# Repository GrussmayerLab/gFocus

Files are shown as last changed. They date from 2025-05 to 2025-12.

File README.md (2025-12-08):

# Fairly Good Focus (fgFocus)

**fgFocus** is an active focus-lock system designed to maintain sharp focus during extended imaging experiments, such as single-molecule and live-cell imaging. It corrects axial drift (movement along the Z-axis) that can occur over time, ensuring your sample stays perfectly in focus.

This project is inspired by similar systems like qgFocus and pgFocus and follows the same naming convention.

Estimated cost for this project is around €160.

## Key Features

- Real-time focus correction  
- Micro-Manager compatible  
- Flexible hardware support: works with any motorized Z-stage controllable through Micro-Manager  

## How It Works

1. An infrared laser beam is aimed slightly off-center into the objective lens.  
2. The beam reflects off the coverslip (glass slide) at the bottom of the sample.  
3. When the sample moves up or down (axial drift), the reflected beam shifts sideways.  
4. A light-array sensor detects this lateral shift by measuring the intensity profile of the reflected beam.  
5. The system calculates the amount of drift using a Gaussian fit to find the center of the beam.  
6. A feedback loop adjusts the Z-position of the stage to return the beam to its original position — restoring focus. 

---

## Table of Contents

* [Fairly Good Focus (fgFocus)](#fairly-good-focus-fgfocus)

  * [Key Features](#key-features)
  * [How It Works](#how-it-works)
  * [Getting Started](#getting-started)
    * [Hardware Setup](#hardware-setup)
    * [Firmware Setup](#firmware-setup)
    * [Software Setup](#software-setup)
  * [Usage](#usage)
  * [Note](#note)
  * [Contribution](#contribution)
  * [License](#license)

---

## Getting Started

### Hardware Setup

1. The **PCB** directory contains the full **Gerber set** for fabrication, plus the **schematic** and **board layout** inside the `fgFocus` subfolder. The project was created in **KiCad**.
2. At **JLCPCB**, upload the `Gerber.rar` archive and select **PCB Assembly**.
3. When prompted, provide the `bom.csv` and `fgFocus-top-pos.csv` files to complete the assembly configuration.
4. Some parts cannot be machine-assembled and must be sourced and soldered manually. These items are listed in `bom_external_components.csv`.
5. The **enclosure design** is located in the `enclosure` directory with a `bom.csv` to source the enclosure. 
6. In the `enclosure` directory you can find a `REAMDE` that explains the assembly of all components.

### Firmware Setup

1. fgFocus uses the [XIAO SAMD21 microcontroller](https://nl.mouser.com/ProductDetail/Seeed-Studio/102010328?qs=GBLSl2AkirtQWO8CTzEK9g%3D%3D&srsltid=AfmBOoqHyFkl2Qpgyily5YNBzPaesjcrrXG1Ro79G8migozdgHgJccld).  
2. Follow this [getting started tutorial](https://wiki.seeedstudio.com/Seeeduino-XIAO/) to program the board using the `fgFocus.ini` file.

### Software Setup

1. **Install Micro-Manager 2.0**  
   - Download and install the latest version of [Micro-Manager 2.0](https://download.micro-manager.org/nightly/2.0/Windows/).  
   - Copy the precompiled `EMU` folder (provided) into the root directory of Micro-Manager.

2. **Install the EMU Plugin** (for editing or customizing the interface)  
   - Follow the instructions here: [EMU Guide](https://jdeschamps.github.io/EMU-guide/)

3. **Install the fgFocus Plugin**  
   - Copy the `FocusLock.jar` file into the `EMU` folder in your Micro-Manager directory.

4. **Install the Device Adapter**  
   - Copy the `mmgr_dal_fgFocus.dll` file into the root directory of Micro-Manager.  
   - To modify or rebuild the adapter:  
     - Follow the [Micro-Manager Visual Studio setup guide](https://micro-manager.org/Visual_Studio_project_settings_for_device_adapters)  
     - Place `.h` files in the **header** folder and `.cpp` files in the **source** folder.  
     - Compile the project and place the resulting `.dll` file into the Micro-Manager root directory.

## Usage

1. Connect the fgFocus system to your PC using a USB-C cable.
2. Create a folder called `fgFocus` in the root of Micro-Manager.  
2. In Micro-Manager, go to **Device > Hardware Configuration Wizard** and create a new config file to only add `fgFocus` and save it in the `fgFocus` folder. Make sure you select a baudrate of 115200.
3. Launch the plugin: **Plugins > User Interface > EMU** — the fgFocus control panel will open. Ignore, the warning that it is not configured, `fgFocus` runs on a separate MMCore instance.

You should see the following interface:

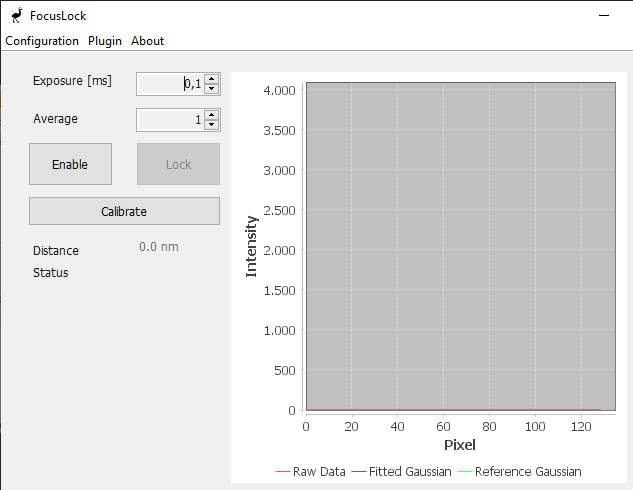
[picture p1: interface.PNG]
fgFocus


Now you're ready to go!

In the interface:
- You can adjust the **exposure time** and **averaging** for the light-array sensor.
- Press the `Enable` button to monitor pixel data from the sensor.
- Use the `Calibrate` button to run a calibration script that determines the relationship between pixel position and Z-distance.
- Once calibration is complete, the `Lock` button becomes available, activating the focus lock.

**Happy Imaging!**

## Note
To adjust the **number of steps** or the **step size** used in the calibration script, open `CalibrateTask.java` and modify the following variables:

```java
private final int numSteps = 5;
private final double stepSizeUm = 1;
```

## Contribution

Contributions are welcome. Whether you're enhancing firmware stability, refining hardware design, or extending the MicroManager plugins, focused pull requests with clear explanations help keep the project maintainable. Open an issue if you'd like to discuss a feature or improvement before implementing it.

## License

Software in this project is licensed under the MIT License and hardware is licensed under CERN OHL - see `LICENSE` file for details in the licenses folder.

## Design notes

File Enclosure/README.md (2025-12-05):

## Assembly Instructions for `fgFocus`

1. **Attach the light sensor**
   Insert the light sensor into the PCB so that the mounting holes on both parts line up correctly.

2. **Install the spacers**
   Place the four spacers onto the mounting posts on the bottom half of the enclosure. These keep the PCB from resting directly on the surface. Ensure the USB-C port is positioned so it lines up with the enclosure’s USB opening.

3. **Insert the bolts**
   From underneath the enclosure, insert the four M3 bolts upward so they pass through the enclosure, the spacers, and the PCB.

4. **Close the enclosure**
   Place the top cover onto the enclosure, then secure it by tightening the provided screws and nuts.

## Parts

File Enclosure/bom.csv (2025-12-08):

enclosure | https://www.digikey.nl/nl/products/detail/hammond-manufacturing/1590LLBBK/2360754
bolts | https://www.amazon.nl/Walfront-Schroefset-koolstofstaal-schroefdraad-gedeeltelijk/dp/B075SDDRVH?__mk_nl_NL=%C3%85M%C3%85%C5%BD%C3%95%C3%91
nuts | https://www.amazon.nl/schroefdraad-zeskantmoeren-koolstofstaal-stopmoeren-zelfborgende/dp/B0C6SM43H6
spacer | https://www.amazon.nl/SWTYExt-afstandhouders-afstandshulzen-wandisolatie-afstandhulzen/dp/B0CWXSTRKZ

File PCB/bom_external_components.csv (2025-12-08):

U7 | XIAO-SAMD21-SAMD21 | https://www.seeedstudio.com/Seeeduino-XIAO-Arduino-Microcontroller-SAMD21-Cortex-M0+-p-4426.html
J3 | DF11-12DS-2DSA(06) | https://eu.mouser.com/ProductDetail/Hirose-Connector/DF11-12DS-2DSA06?qs=Ux3WWAnHpjDo2sVdM55Wrg%3D%3D
Line Sensor | TSL1401-DB | https://abra-electronics.com/robotics-embedded-electronics/parallax-en/parallax-sensors/28317-parallax-tsl1401-linescan-imaging-sensor-daughterboard-28317.html

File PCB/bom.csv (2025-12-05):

Comment | Designator | Footprint | LCSC
1.5k" | R5 | Resistor_SMD:R_0805_2012Metric | C4310
100p | C15 | Capacitor_SMD:C_0805_2012Metric | C1790

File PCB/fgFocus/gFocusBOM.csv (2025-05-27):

Reference | Value | Datasheet | Footprint | Qty | DNP
C1,C2,C5,C6,C7,C20,C21,L1,L2 | 10u | ~ | -- mixed values -- | 9
C3,C4,C24 | 10n | ~ | Capacitor_SMD:C_0805_2012Metric | 3
C8,C9,C10,C12,C14,C17,C18,C19 | 100n | ~ | Capacitor_SMD:C_0805_2012Metric | 8
C15 | 100p | ~ | Capacitor_SMD:C_0805_2012Metric | 1
C16,C22,C23 | 1u | ~ | Capacitor_SMD:C_0805_2012Metric | 3
C25 | 4.5n | ~ | Capacitor_SMD:C_0805_2012Metric | 1
D1 | PMEG2005EL | ~ | Diode_SMD:D_SOD-882 | 1
J1 | FTSH-105-01-F-DV-P-TR |  | FTSH-105-01-F-DV-P-TR:SAMTEC_FTSH-105-01-F-DV-P-TR | 1
J2 | Conn_Coaxial | ~ | Connector_Coaxial:SMA_Amphenol_132289_EdgeMount | 1
J3 | Conn_02x06_Counter_Clockwise | ~ | Connector_Hirose:Hirose_DF11-12DP-2DSA_2x06_P2.00mm_Vertical | 1
J4 | USB_B_Micro | ~ | Connector_USB:USB_Micro-B_Molex-105017-0001 | 1
R1,R4,R6,R7 | 10k | ~ | Resistor_SMD:R_0805_2012Metric | 4
R2,R3 | 93.1k | ~ | Resistor_SMD:R_0805_2012Metric | 2
R5 | 1.5k | ~ | Resistor_SMD:R_0805_2012Metric | 1
R8 | 1M | ~ | Resistor_SMD:R_0805_2012Metric | 1
U1 | NMA0515SC | http://power.murata.com/data/power/ncl/kdc_nma.pdf | Converter_DCDC:Converter_DCDC_Murata_NMAxxxxSC_THT | 1
U2 | TPS7A3001DGNT |  | TPS7A3001DGNT:SOP65P490X110-9N | 1
U3 | TPS7A4901DGNR |  | TPS7A3001DGNT:SOP65P490X110-9N | 1
U4 | AD5761RBRUZ-RL7 |  | AD5761RBRUZ-RL7:SOP65P640X120-16N | 1
U5 | ATSAMD21G18A-A | http://ww1.microchip.com/downloads/en/DeviceDoc/SAM_D21_DA1_Family_Data%20Sheet_DS40001882E.pdf | Package_QFP:TQFP-48_7x7mm_P0.5mm | 1
U6 | IP4234CZ6 | https://assets.nexperia.com/documents/data-sheet/IP4234CZ6.pdf | Package_TO_SOT_SMD:SOT-23-6 | 1
U8 | LDK130-32_SOT23_SOT353 | http://www.st.com/content/ccc/resource/technical/document/datasheet/29/10/f7/87/2f/66/47/f4/DM00076097.pdf/files/DM00076097.pdf/jcr:content/translations/en.DM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 | Package_TO_SOT_SMD:SOT-23-5_HandSoldering | 1

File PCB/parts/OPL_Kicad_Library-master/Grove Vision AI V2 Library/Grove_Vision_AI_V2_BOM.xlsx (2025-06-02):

Layer Jump | Number | Name | Specification | Operating Temperature | MPN Code | Quantity | Base | Plug Position | Process
N | 301010000 | SMD RES 0R-5%-1/16W;0402 |  | -55°C to 155°C | RC0402JR-070RL | 3 | 1 | R29,R30,R39 | SMT1
N | 301010004 | SMD RES 10K-5%-1/16W;0402 |  | -55°C to 155°C | RC0402JR-0710KL | 7 | 1 | R5,R7,R8,R23,R24,R31,R38 | SMT1
N | 301010008 | SMD RES 510K-5%-1/16W;0402 |  | -55°C to 155°C | RC0402JR-07510KL | 1 | 1 | R35 | SMT1
N | 301010456 | SMD RES 100K-1%-1/16W;0402 |  | -55°C to 155°C | RC0402FR-07100KL | 7 | 1 | R6,R10,R11,R16,R32,R33,R37 | SMT1
N | 301010495 | SMD RES;5.1K-1%-1/16W;0402 |  | -55°C to 155°C | RC0402FR-075K1L | 3 | 1 | R2,R3,R36 | SMT1
N | 301010746 | SMD RES 2.2K-1%-1/16W;0402 |  | -55°C to 155°C | RC0402FR-072K2L | 10 | 1 | R1,R4,R13,R14,R15,R19,R20,R21,R22,R40 | SMT1
N | 301011331 | SMD RES 22.1K-1%-1/16W;0402 |  | -55°C to 155°C | RC0402FR-0722K1L | 2 | 1 | R26,R34 | SMT1
N | 302010004 | SMD CAP Ceramic 100nF-16V-10%-X7R;0402 |  | -55°C to 125°C | CC0402KRX7R7BB104 | 18 | 1 | C5,C8,C13,C20,C21,C22,C23,C24,C25,C26,C27,C29,C30,C31,C32,C35,C36,C39 | SMT1
N | 302010006 | SMD CAP Ceramic 10nF-50V-10%-X7R;0402 |  | -55°C to 125°C | CC0402KRX7R9BB103 | 1 | 1 | C3 | SMT1
N | 302010049 | SMD CAP Ceramic 12pF-50V-5%-NPO;0402 |  | -55°C to 125°C | CC0402JRNPO9BN120 | 2 | 1 | C14,C15 | SMT1
N | 302010051 | SMD CAP Ceramic 220nF-16V-10%-X7R;0402 |  | -55°C to 125°C | CC0402KRX7R7BB224 | 1 | 1 | C16 | SMT1
N | 302010407 | SMD CAP Ceramic 4.7uF-10V-10%-X5R;0402 |  | -55°C to 85°C | CC0402KRX5R6BB475 | 7 | 1 | C4,C6,C7,C9,C10,C28,C34 | SMT1
N | 302010519 | SMD CAP Ceramic 10uF-10V-20%-X5R;0402 |  | -55°C to 85°C | CC0402MRX5R6BB106 | 2 | 1 | C11,C37 | SMT1
N | 302013249 | SMD CAP Ceramic 1uF-10V-10%-X5R;0402 |  | -55°C to 85°C | CL05A105KP5NNNC | 5 | 1 | C1,C2,C17,C18,C19 | SMT1
N | 303010544 | SMD Inductor 4.7uH-20%-1.1A;0806 |  | -40°C to 105°C | VLS201610HBX-4R7M-1 | 1 | 1 | L1 | SMT1
N | 303011858 | SMD Inductor 470nH-20%-2.6A;0603 |  | -40°C to 125°C | TFM160808ALC-R47MTAA | 2 | 1 | L2,L3 | SMT1
N | 304011053 | SMD Diode Schottky 40V-1A;SOD-323 |  |  | B5819WS SL | 4 | 1 | D1,D2,D3,D4 | SMT1
N | 304090121 | SMD LED Clear-Green;0402 | As posted |  | BL-HGE37A-AV-TRB | 1 | 1 | LED2 | SMT1
N | 304090746 | SMD LED Clear-Yellow;0402 | As posted |  | 16-213/Y2C-AN2Q1B/3T | 1 | 1 | LED1 | SMT1
N | 305030071 | SMD MOSFET N-CH 20V-500mA;SOT-523 |  |  | CJ1012 | 5 | 1 | Q1,Q2,Q3,Q4,Q5 | SMT1
N | 306011444 | SMD Crystal;24MHz-12pF-10ppm-4P-2.0*1.6*0.5mm |  | -40°C to 85°C | Y2400FE001 | 1 | 1 | X1 | SMT1
N | 310011697 | SMD IC MCU;Dual Cortex-M55 Core(Max 400MHz)-With a 400MHz NPU;WLCSP-65 | L5.58*W2.27mm | -40°C to 85°C | HX6538-A01TWA | 1 | 1 | U1 | SMT1
N | 310032794 | SMD IC PMIC;DCDC Buck-ADJ-2.2MHz-4A;DFN1.5×1.5-6 |  | -40°C to 85°C | SY80004DQD | 2 | 1 | U4,U6 | SMT1
N | 310032813 | SMD IC PMIC;LDO-1.8V-300mA;XTDFN-1*1-4L |  | -40°C to 125°C | SGM2036S-1.8XXDH4G/TR | 1 | 1 | U3 | SMT1
N | 310071431 | SMD IC Interface USB to High Speed TTL;QFN16 | USB to High-Speed Serial Port | -40°C to 85°C | CH343P | 1 | 1 | U2 | SMT1
N | 310091468 | SMD IC Memory;128Mbit-1.8V;SOIC-8 |  | -40°C to 85°C | W25Q128JWSIQ | 1 | 1 | U5 | SMT1
N | 311020009 | SMD Top Button 4N;4P-L4.6*W3.2*H2.5mm |  | -20°C to 70°C | SKRPADE010 | 1 | 1 | RST1 | SMT1
N | 311020518 | SMD Top Button 1.57N;4P-L4.6*W3.2*H2.5mm |  | -30°C to 85°C | SKRPABE010 | 1 | 1 | BOOT1 | SMT1
N | 312030502 | SMD DIGITAL MIC OMNI -26dBFS;OCLGA-4:3.5*2.65*0.94mm |  | -40˚C to 100˚C | MSM261D3526H1CPM | 1 | 1 | MIC1 | SMT1
N | 319015667 | PCB;Grove - Vision AI Module V2 -蓝油白字-4层 | 20*40*1.6mm-ENIG-FR4;Steel mesh code；404012305 |  |  | 1 | 1 |  | SMT1
N | 320011358 | SMD USB TYPE C-W/P;12+4P-8.94*7.35*3.26mm |  | -30°C to 85°C | USB-31C-F-16P-L7.35 | 1 | 1 | J1 | SMT1
N | 320031231 | DIP Black Female Header VERT;1*7P-2.54-5.0mm |  | -40℃ to 105℃ |  | 2 | 1 | P8,P9 | Unit
N | 320060904 | SMD FPC CONN Bottom Contact;15P-1.0mm;L19.9*W6.76*H2.0mm |  | -30°C to 85°C | ST-FPC-W102015-D | 1 | 1 | J2 | SMT1
N | 320090535 | SMD uSD Card Holder;9+4P-L11.25*W6.96*H1.42mm |  | -25°C to 70°C | ST-TF-MR267 | 1 | 1 | J5 | SMT1
N | 320110032 | SMD Grove Female Header-Beige;4P-2.0-90D | 2.0-4PHorizontal Mount with Locking Socket |  | PHS-4A horizontal mount | 1 | 1 | J3 | SMT1

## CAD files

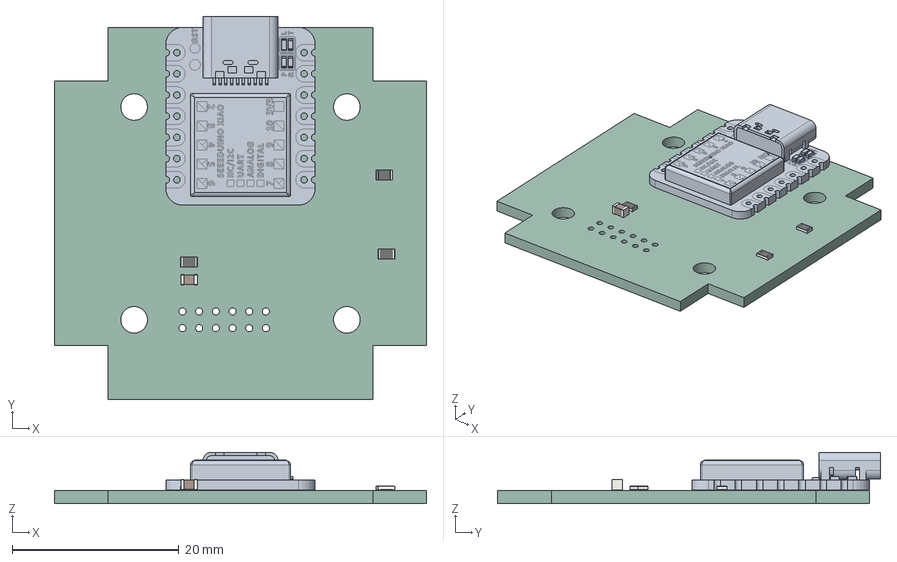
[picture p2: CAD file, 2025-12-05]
PCB/fgFocus/fgFocus.step
44.6 x 45.9 x 6.15 mm
Seeeduino XIAO SAMD21 v4
R_0805_2012Metric x 3
C_0805_2012Metric
gFocus_PCB

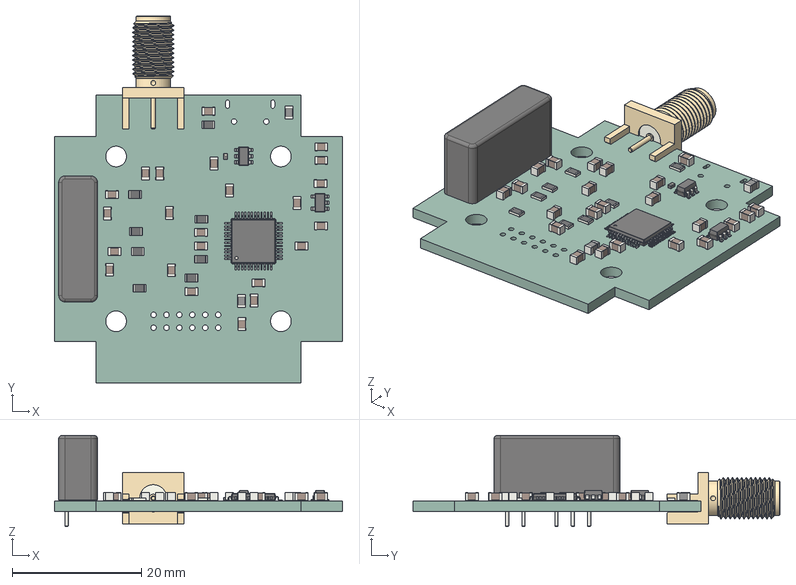
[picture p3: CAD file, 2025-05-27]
PCB/gFocus/gFocus.step
44.6 x 56.8 x 14.1 mm
Converter_DCDC_muRata_NMAxxxxSC_THT
C_0805_2012Metric x 23
R_0805_2012Metric x 8
SOT_23_6
TQFP_48_7x7mm_P05mm
D_SOD-882
L_0805_2012Metric x 2
SOT_23_5
SMA_Amphenol_132289_EdgeMount
_autosave-gFocus_PCB

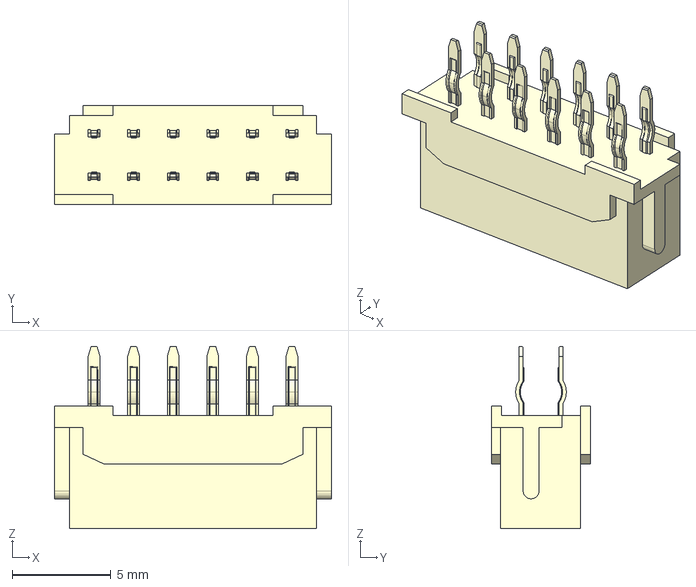
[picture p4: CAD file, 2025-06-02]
PCB/parts/DF11-12DS-2DSA--3DModel-STEP-1.STEP
14.0 x 5.00 x 9.20 mm

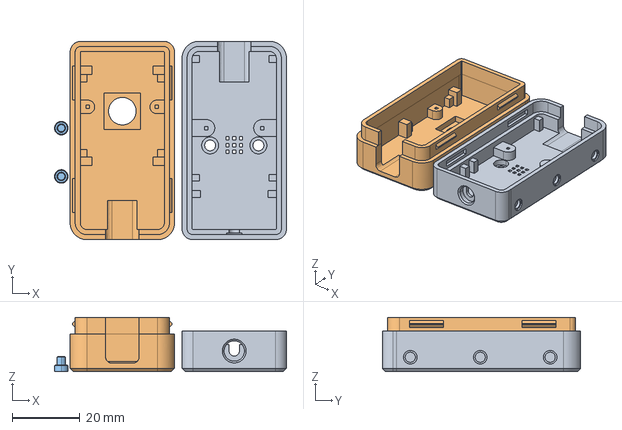
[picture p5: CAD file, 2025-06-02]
PCB/parts/OPL_Kicad_Library-master/Grove Vision AI V2 Library/himax.stp
68.4 x 58.5 x 16.1 mm

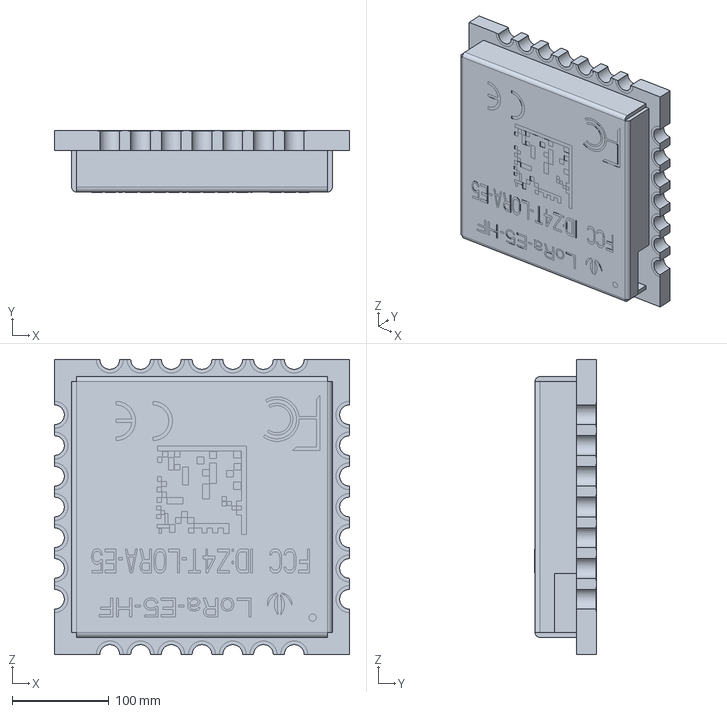
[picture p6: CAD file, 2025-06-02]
PCB/parts/OPL_Kicad_Library-master/Seeed Studio Wio Series/Wio-E5-LE/LoRa-E5-LE-HF_3D_File.stp
304.8 x 63.8 x 304.8 mm

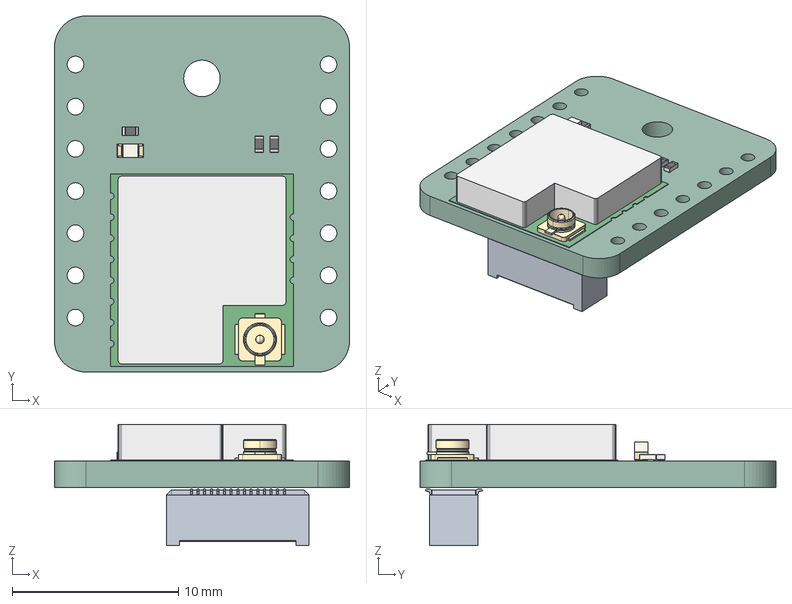
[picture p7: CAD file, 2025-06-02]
PCB/parts/OPL_Kicad_Library-master/Seeed Studio Wio Series/Wio-SX1262/Wio-SX1262_for_XIAO_3D_file.step
17.8 x 21.4 x 7.30 mm
R_0402_1005Metric x 3
LED_0603_1608Metric
PCB
BF04-30pin-35H
Wio-SX1262 for XIAO V1.0_PCB

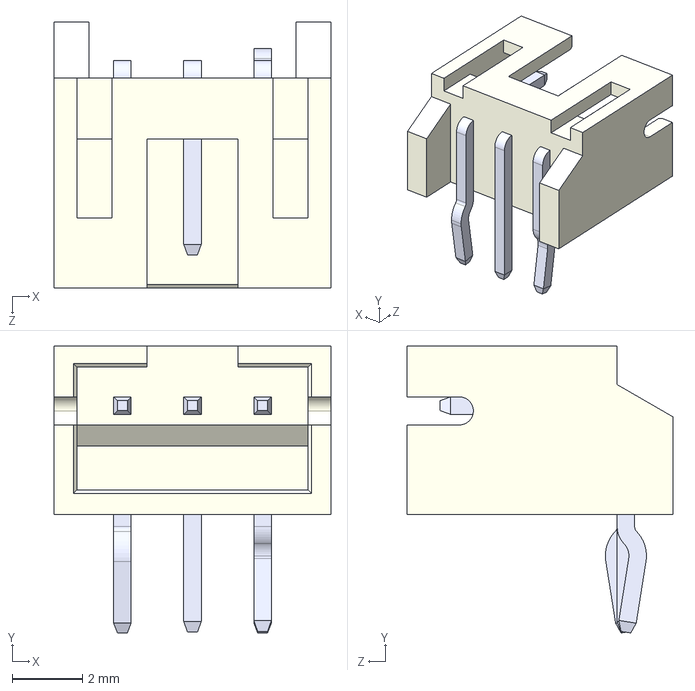
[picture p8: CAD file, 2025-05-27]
PCB/parts/S3B-PH-K-S_LF__SN_.step
7.90 x 8.18 x 7.60 mm

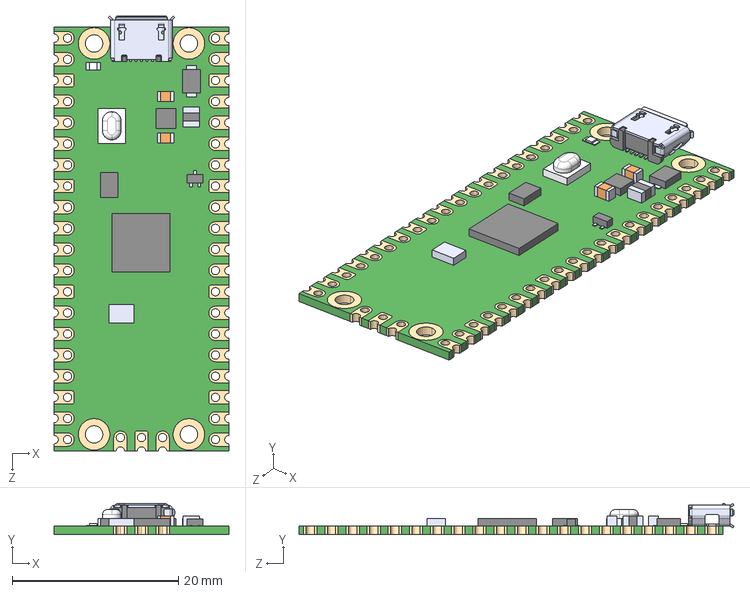
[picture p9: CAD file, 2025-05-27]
PCB/parts/SC0915.step
21.0 x 3.73 x 52.3 mm

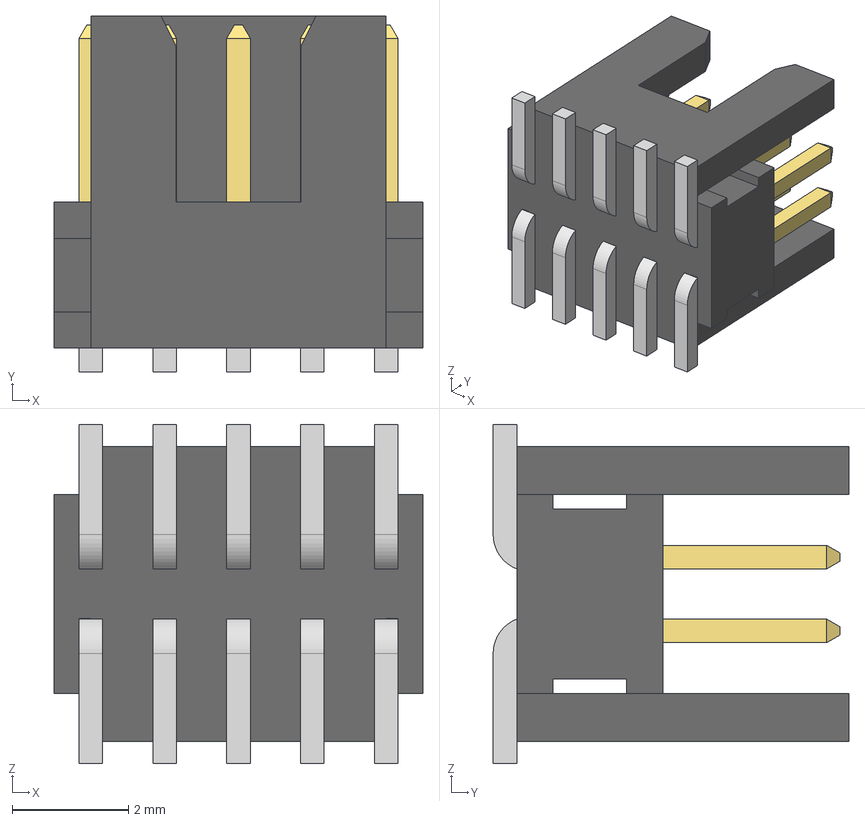
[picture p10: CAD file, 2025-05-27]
PCB/parts/FTSH-105-01-F-DV-P-TR.step
6.35 x 6.12 x 5.84 mm
FTSH-105-01-F-DV-K_body
FTSH-105-01-F-DV-K_pins1
FTSH-105-01-F-DV-K_pins2

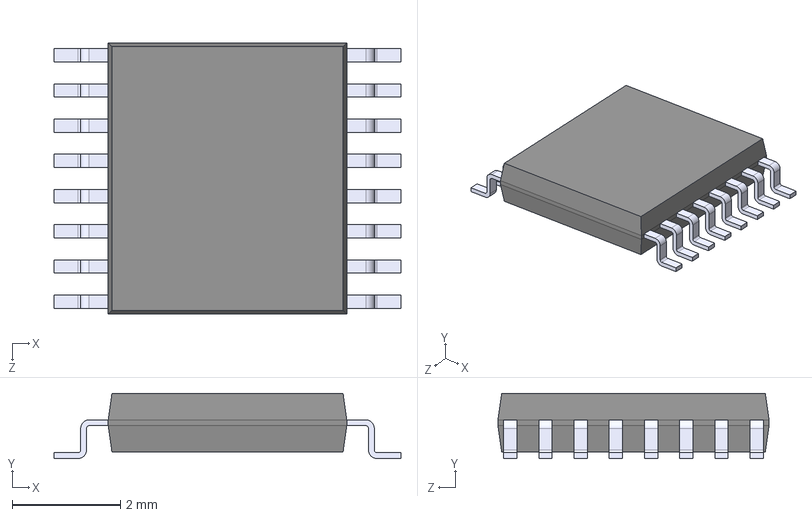
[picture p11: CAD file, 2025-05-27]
PCB/parts/AD5761RBRUZ-RL7.step
6.40 x 1.20 x 5.00 mm

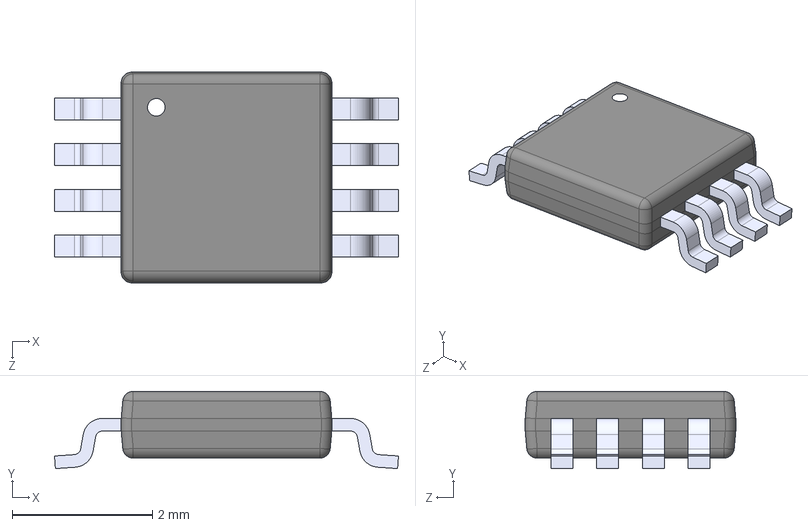
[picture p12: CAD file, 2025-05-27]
PCB/parts/TPS7A3001DGNT.step
4.90 x 1.10 x 3.00 mm

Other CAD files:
PCB/parts/OPL_Kicad_Library-master/Grove Vision AI V2 Library/himax.3mf

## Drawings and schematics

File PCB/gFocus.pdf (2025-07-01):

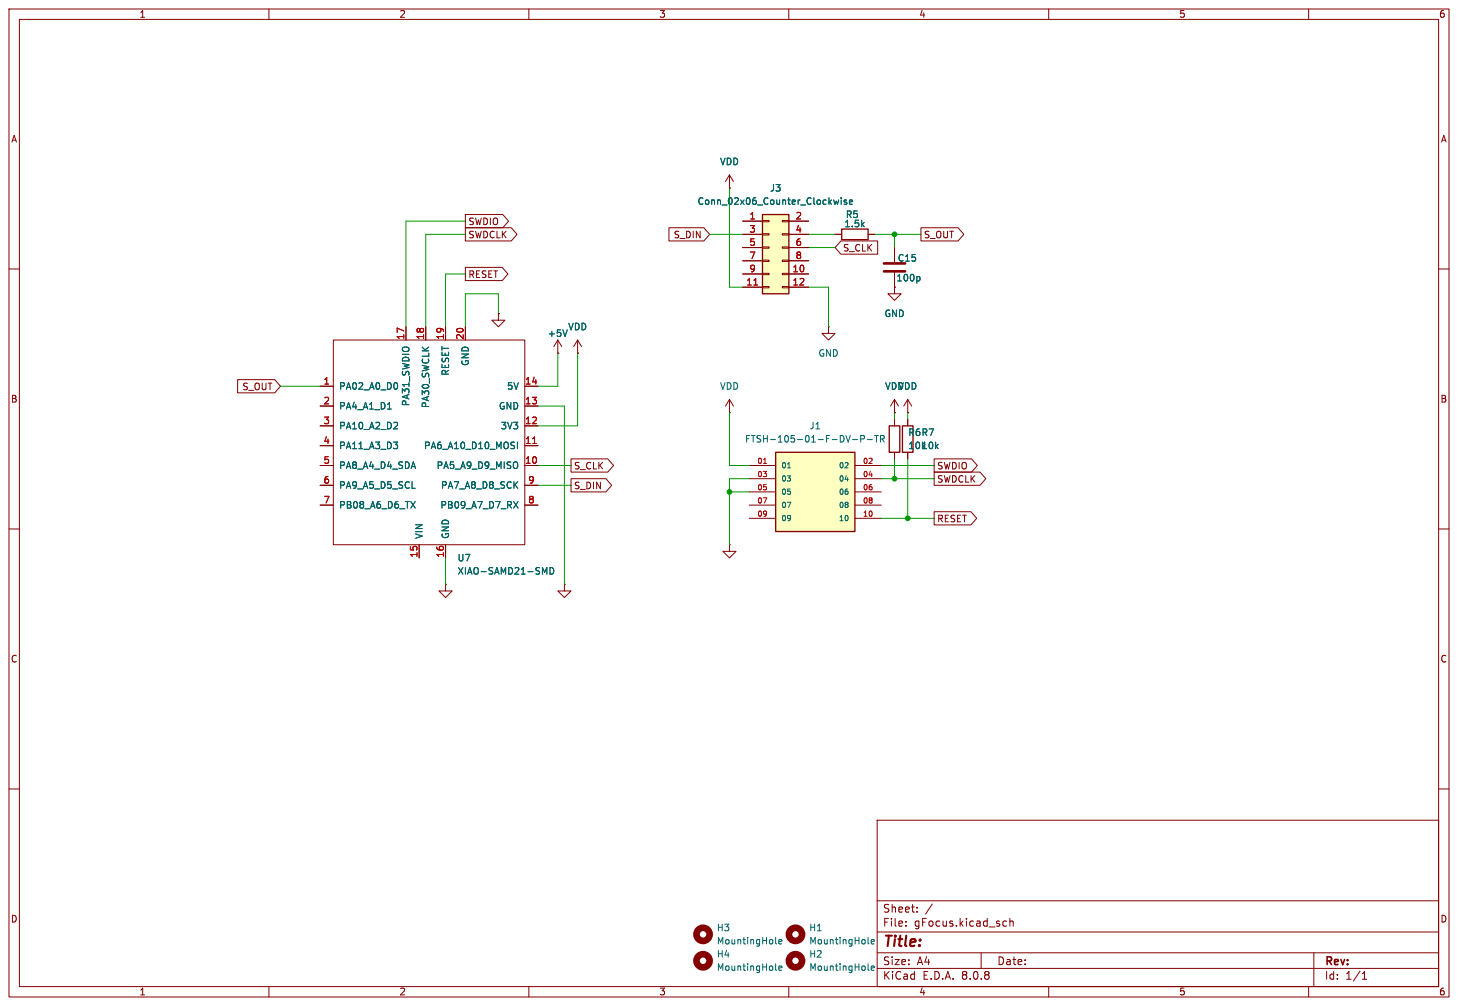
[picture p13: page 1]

Id: 1/1 Title: File: gFocus.kicad_sch Sheet: /

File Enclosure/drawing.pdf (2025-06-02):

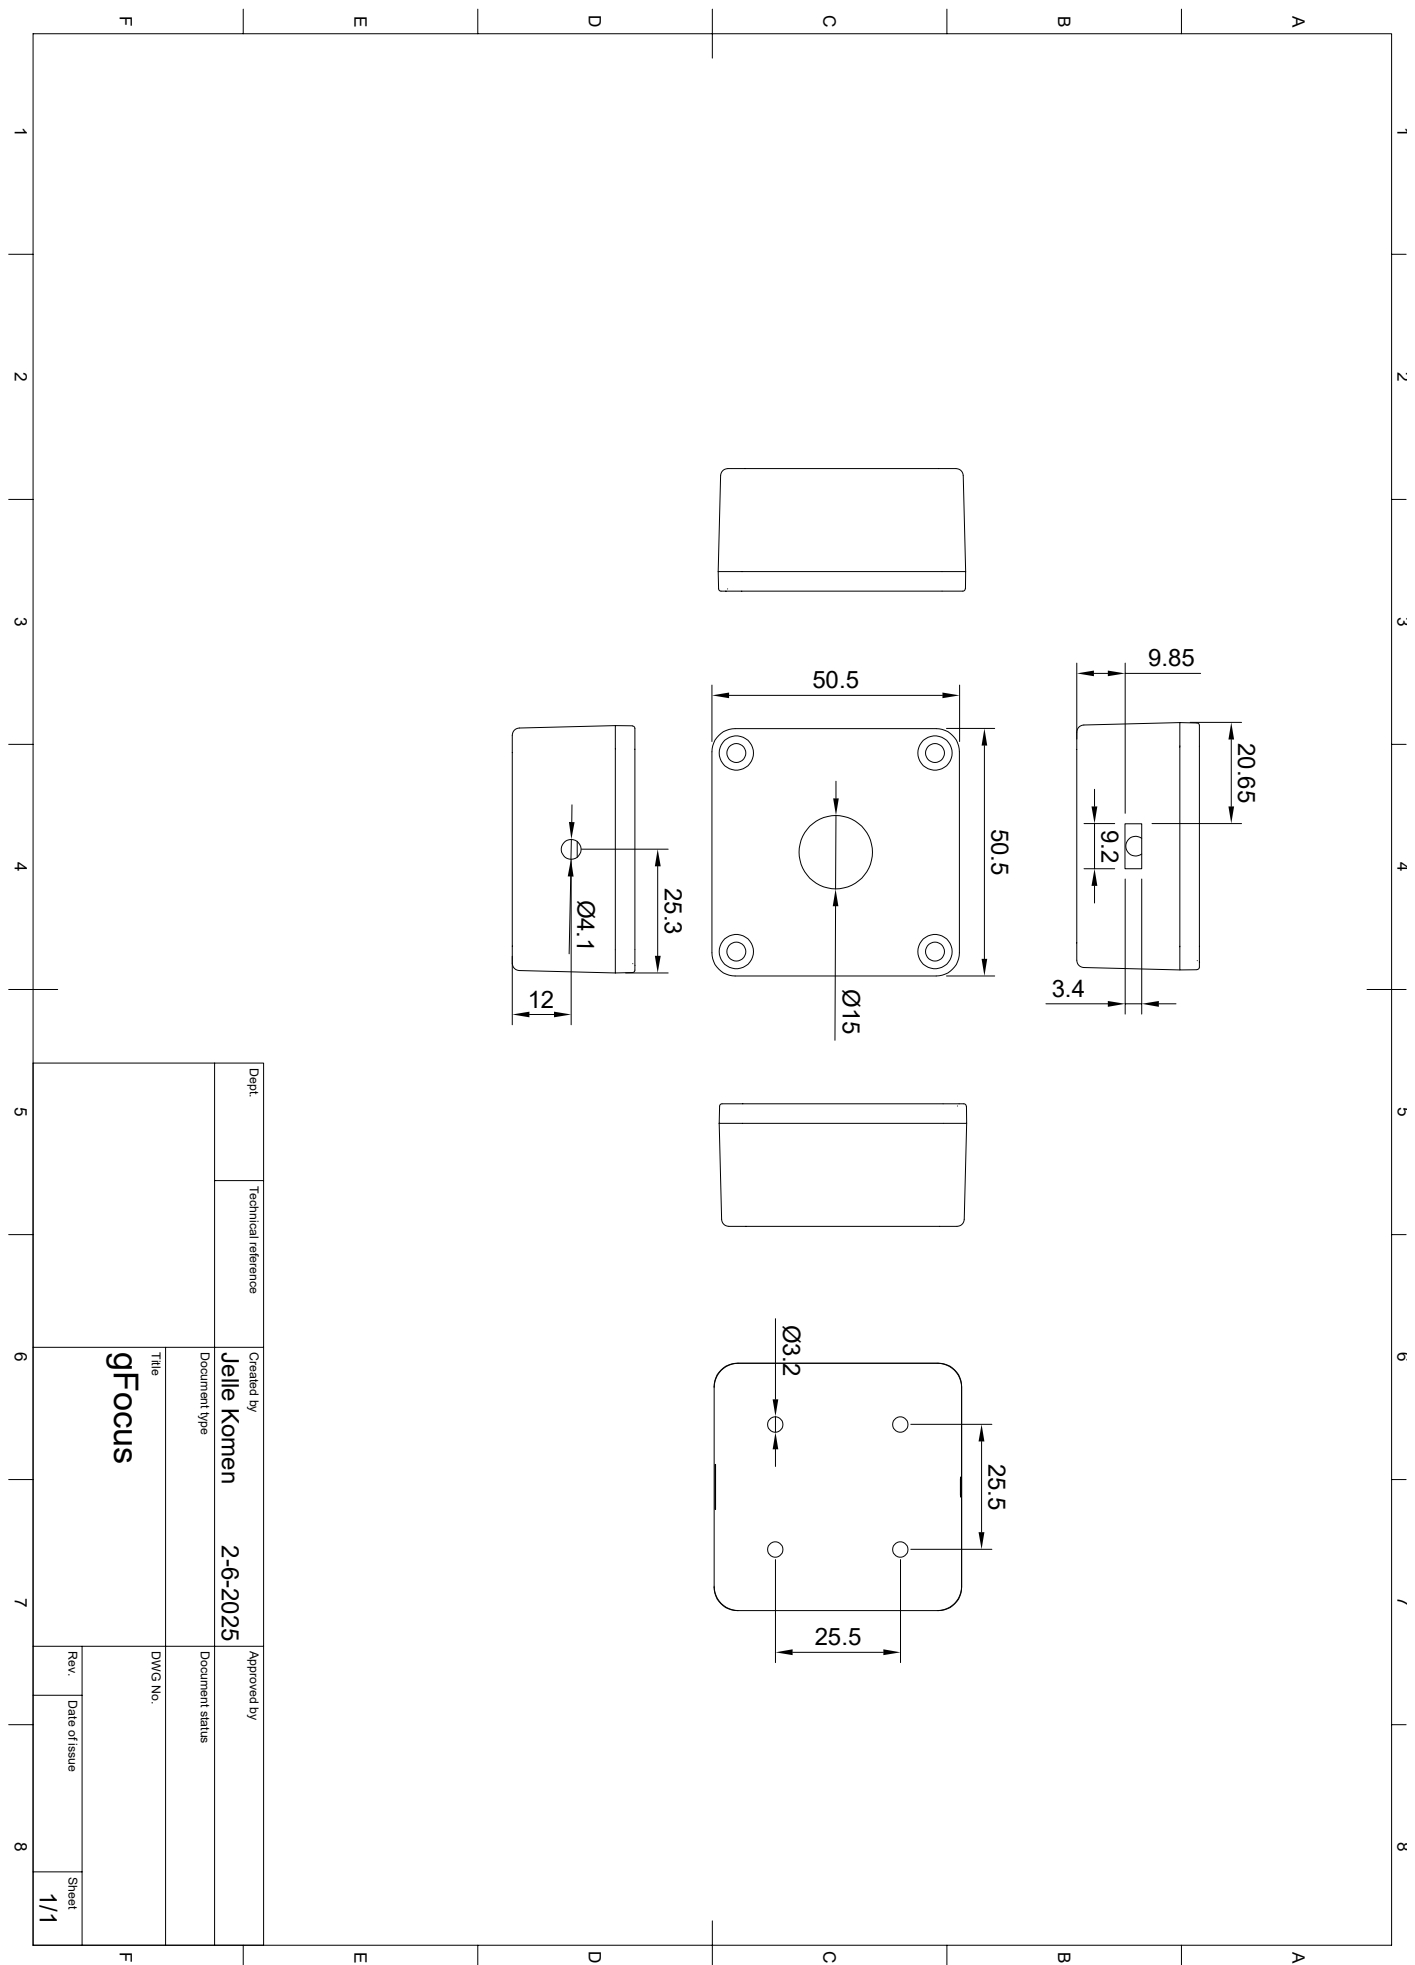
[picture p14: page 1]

1 A 2 3 4 5 6 7 8 1 2 3 4 5 6 7 8 FEDCB FEDCBA Dept. Technical reference Created by Approved by Title DWG No. Document type Document status Rev. Date of issue Sheet 2-6-2025 1/1 gFocus Jelle Komen Ø3.2

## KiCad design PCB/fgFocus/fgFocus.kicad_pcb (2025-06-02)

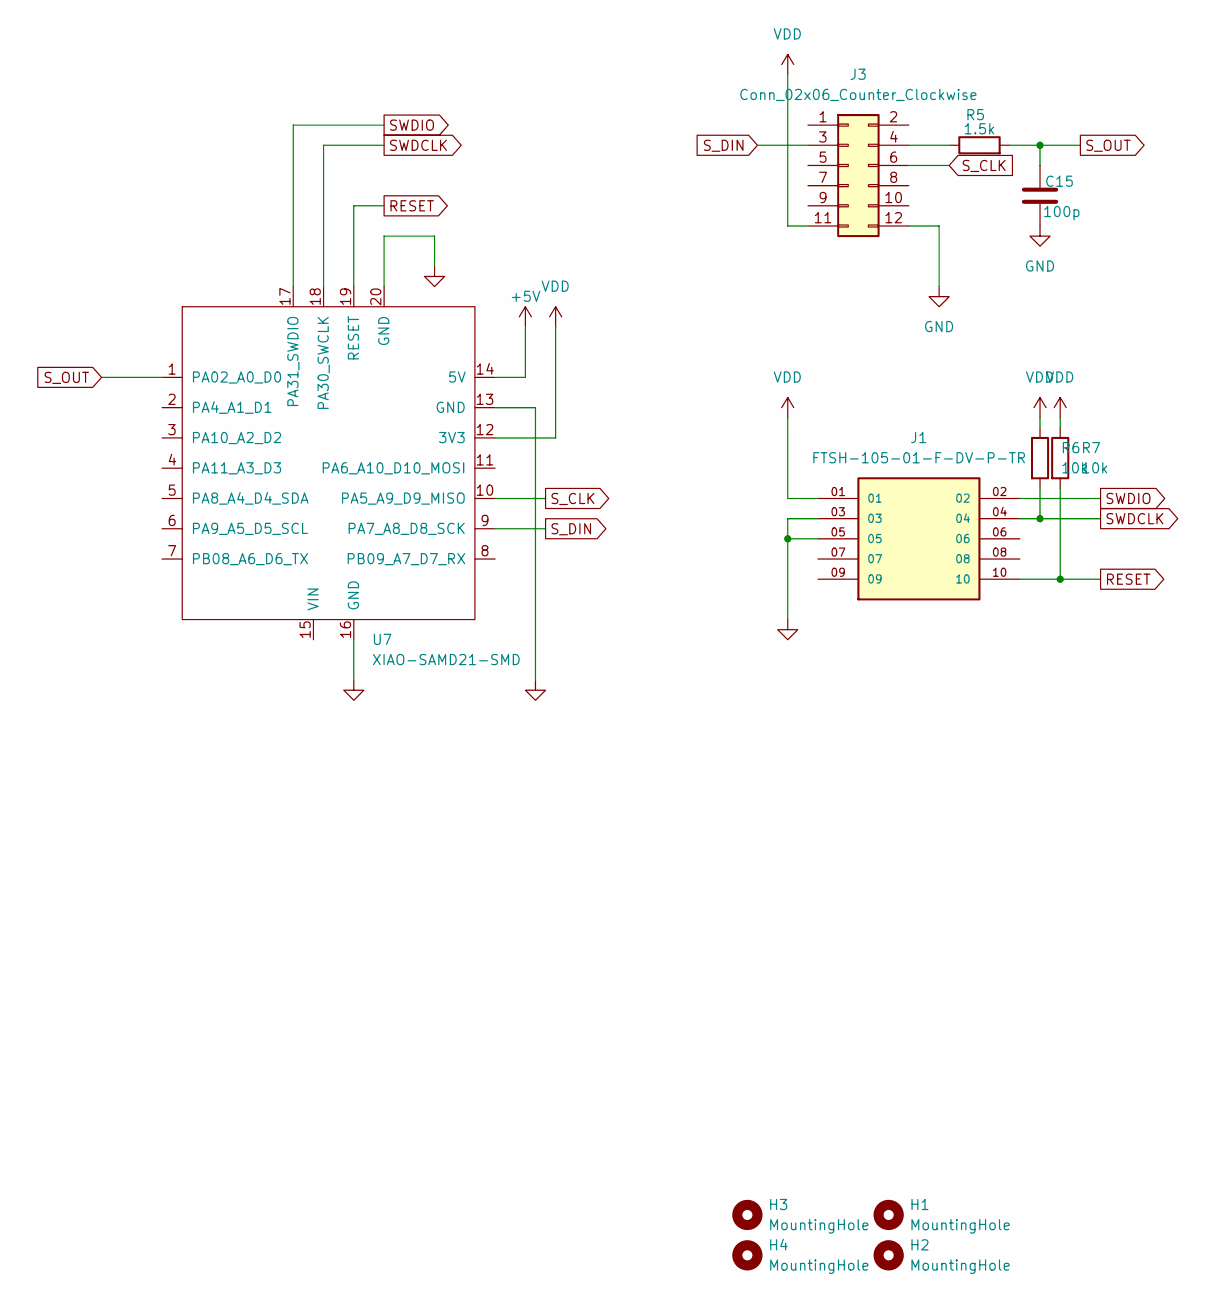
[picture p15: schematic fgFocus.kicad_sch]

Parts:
C15: 100p; C_0805_2012Metric
H1, H2, H3, H4: MountingHole; MountingHole_3.2mm_M3
J1: FTSH-105-01-F-DV-P-TR; SAMTEC_FTSH-105-01-F-DV-P-TR; PARTREV R
J3: Conn_02x06_Counter_Clockwise; Hirose_DF11-12DP-2DSA_2x06_P2.00mm_Vertical
R5: 1.5k; R_0805_2012Metric
R6, R7: 10k; R_0805_2012Metric
U7: XIAO-SAMD21-SMD

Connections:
+5V: U7.14 (5V)
GND: C15.2, J1.03, J1.05, J3.12, U7.13 (GND), U7.16 (GND), U7.20 (GND)
unnamed: J3.4, R5.1
RESET: J1.10, R7.2, U7.19 (RESET)
SWDCLK: J1.04, R6.2, U7.18 (PA30_SWCLK)
SWDIO: J1.02, U7.17 (PA31_SWDIO)
S_CLK: J3.6, U7.10 (PA5_A9_D9_MISO)
S_DIN: J3.3, U7.9 (PA7_A8_D8_SCK)
S_OUT: C15.1, R5.2, U7.1 (PA02_A0_D0)
VDD: J1.01, J3.11, R6.1, R7.1, U7.12 (3V3)

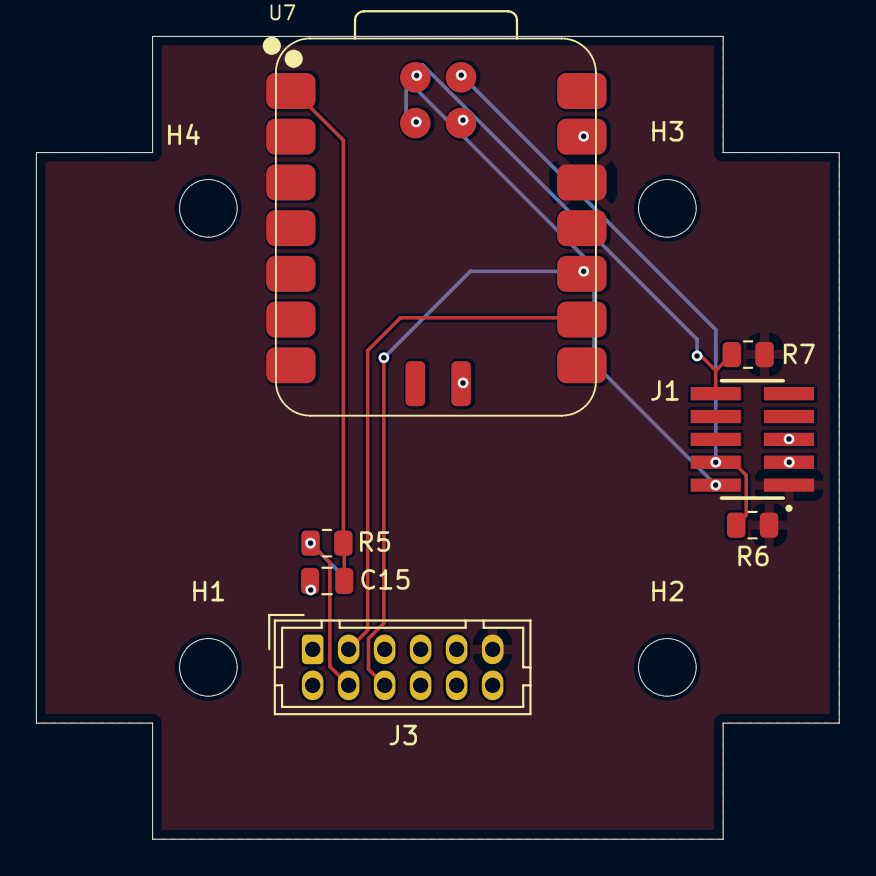
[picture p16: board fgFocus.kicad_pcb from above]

Board: 2 copper layers, 44.6 x 44.6 mm, 11 parts (0 on the bottom side), 9 nets.

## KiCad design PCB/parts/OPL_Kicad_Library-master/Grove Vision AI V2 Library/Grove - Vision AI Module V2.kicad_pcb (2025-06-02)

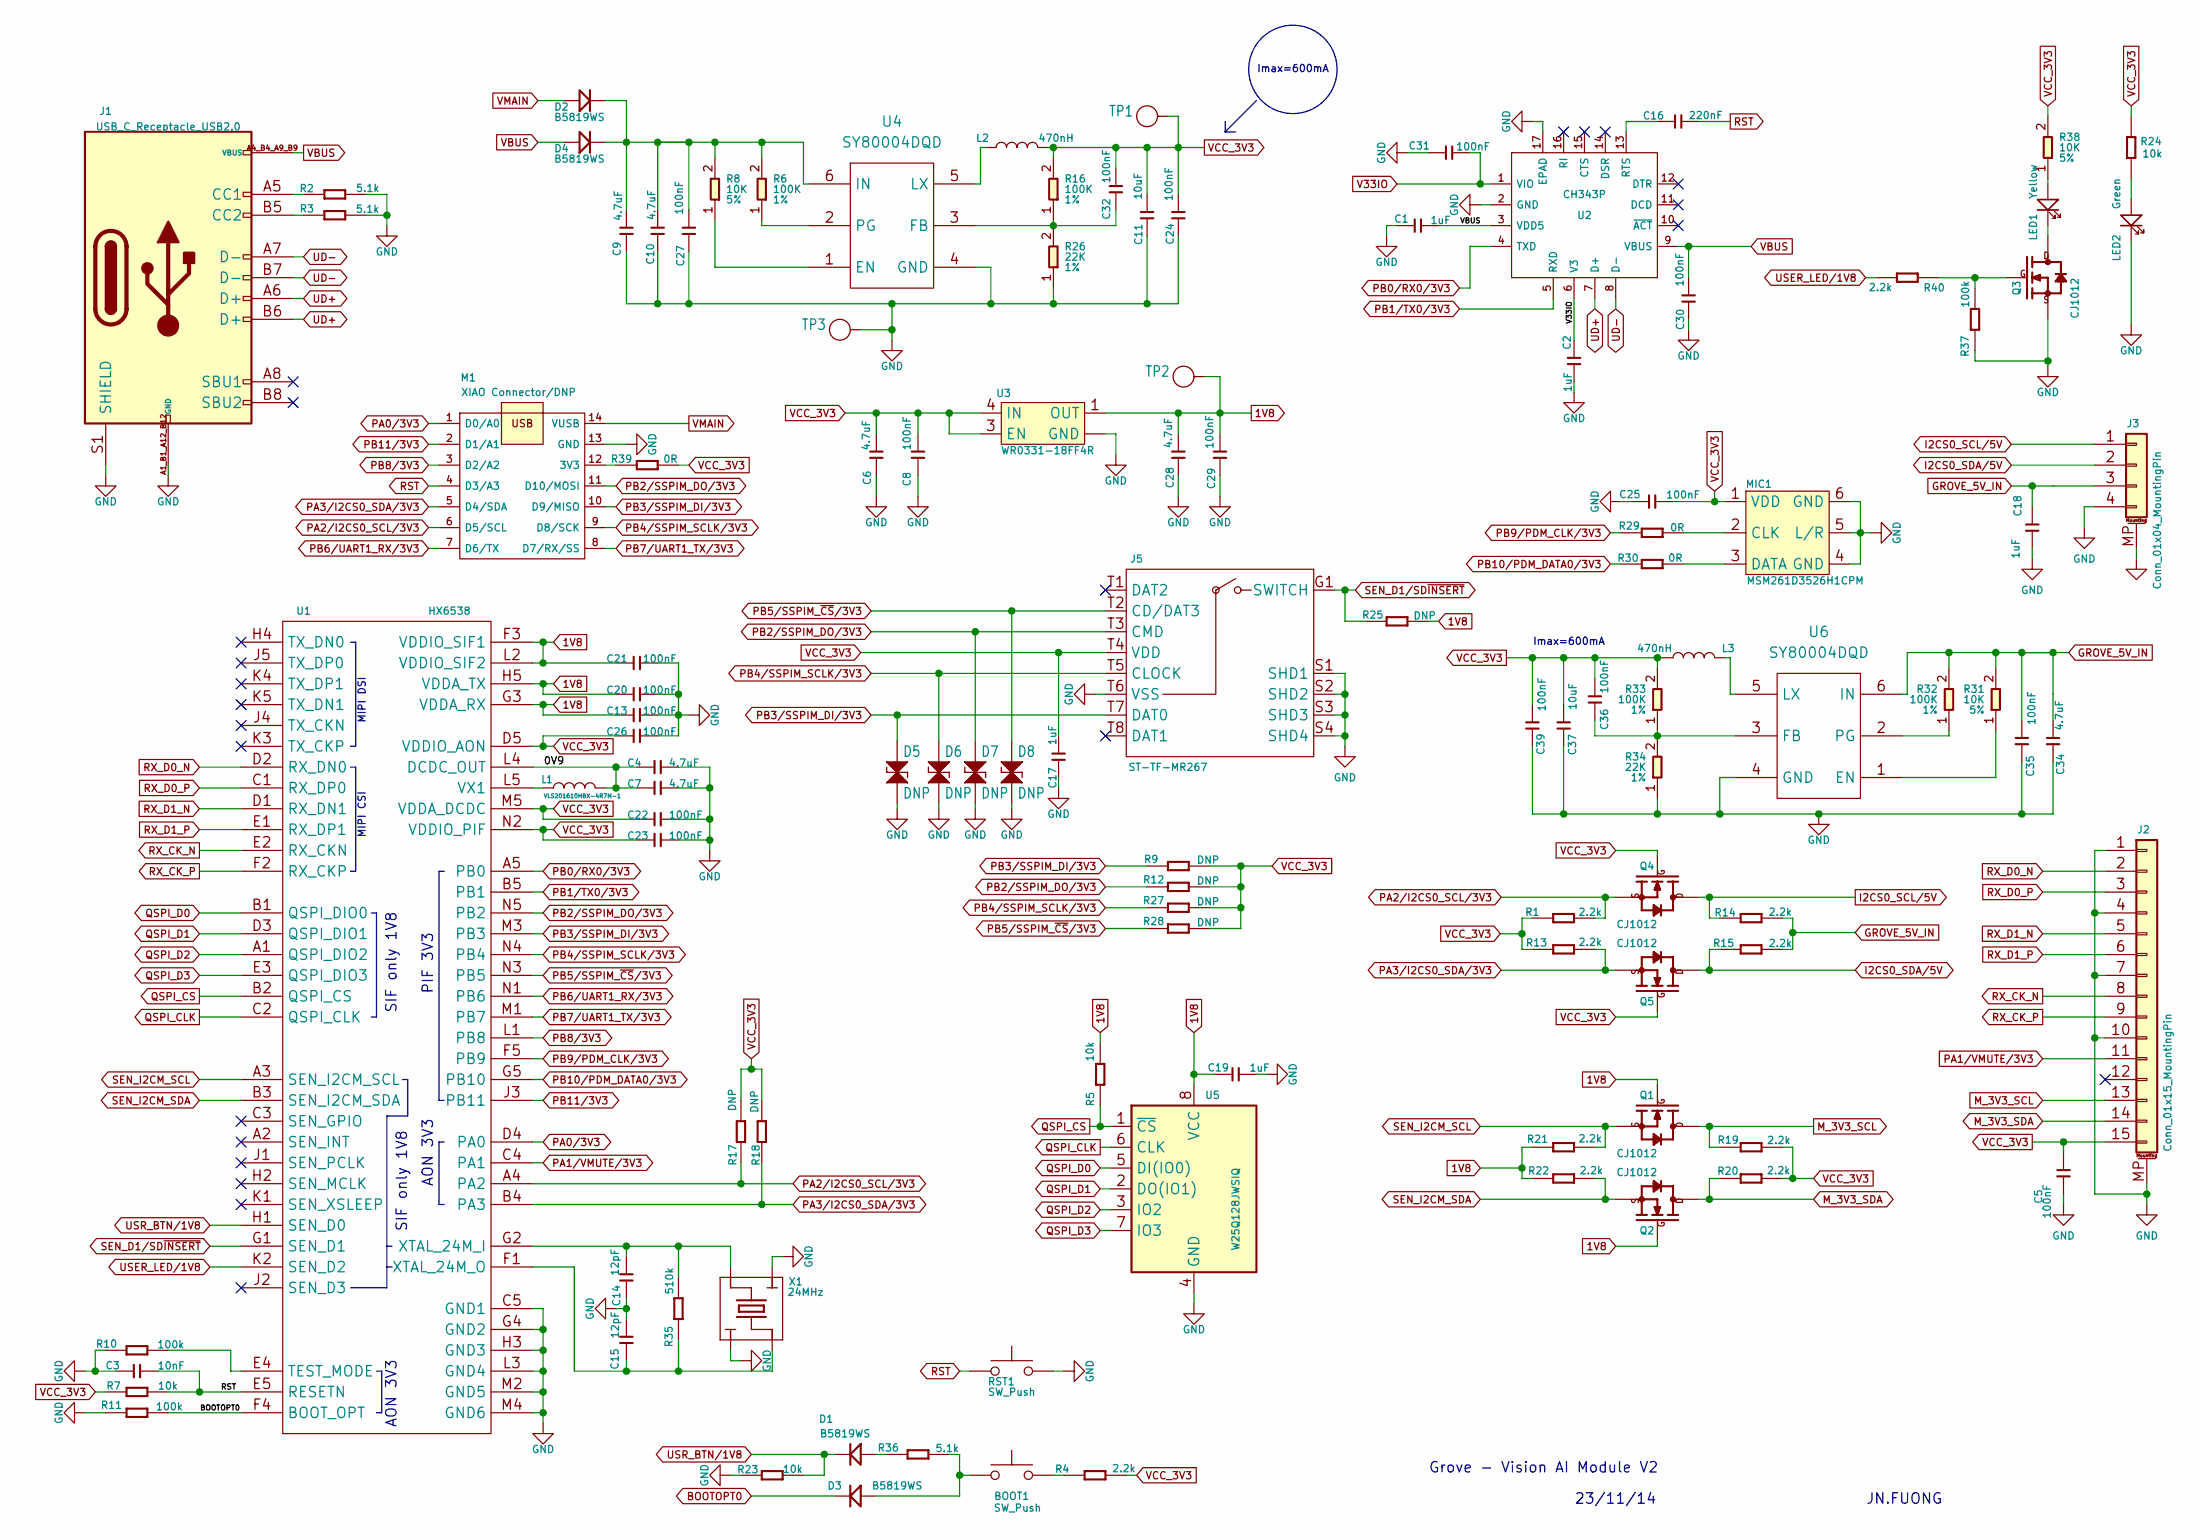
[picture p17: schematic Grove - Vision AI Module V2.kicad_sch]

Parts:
BOOT1: SW_Push; SW_Push_1P1T_NO_Vertical_Wuerth_434133025816
C1, C2, C17, C18, C19: 1uF; C0402
C3: 10nF; C0402
C4, C6, C7, C9, C10, C28, C34: 4.7uF; C0402
C5, C8, C13, C20, C21, C22, C23, C24, C25, C26, C27, C29, C30, C31, C32, C35, C36, C39: 100nF; C0402
C11, C37: 10uF; C0402
C14, C15: 12pF; C0402
C16: 220nF; C0402
D1, D2, D3, D4: B5819WS; D0805_SOD323
D5, D6, D7, D8: DNP; R0402; MPN DF2S6.8FS
J1: USB_C_Receptacle_USB2.0; USB2.0-TYPE-C
J2: Conn_01x15_MountingPin; FPC_DNC_15P_1.0mm
J3: Conn_01x04_MountingPin; 4P-SMD-2.0mm-RIGHT
J5: ST-TF-MR267; SD-TF-MR267; MPN SD-TF-MR267
L1: VLS201610HBX-4R7M-1; L0806
L2, L3: 470nH; L0603
LED1: Yellow; LED0402
LED2: Green; LED0402
M1: XIAO Connector/DNP; XIAO_Socket
MIC1: MSM261D3526H1CPM; MIC6P-3.5X2.65X0.94MM
Q1, Q2, Q3, Q4, Q5: CJ1012; SOT523
R1, R4, R13, R14, R15, R19, R20, R21, R22, R40: 2.2k; R0402
R2, R3, R36: 5.1k; R0402
R5, R7, R23, R24: 10k; R0402
R6, R16, R32, R33: 100K; R0402; Power Rating 1%; MPN RC0402JR-074K7L
R8, R31, R38: 10K; R0402; Power Rating 5%; MPN RC0402JR-074K7L
R9, R12, R17, R18, R25, R27, R28: DNP; R0402
R10, R11, R37: 100k; R0402
R26, R34: 22K; R0402; Power Rating 1%; MPN RC0402JR-074K7L
R29, R30, R39: 0R; R0402
R35: 510k; R0402
RST1: SW_Push; SW_Push_1P1T_NO_Vertical_Wuerth_434133025816
TP1, TP2, TP3: Test Point; TP-D35MIL; Part Type Test Point
U1: HX6538; WLCSP65_5.6x2.3x0.56mm
U2: CH343P; QFN-16-EP_3x3mm_P0.5mm_EP1x1mm
U3: WR0331-18FF4R; X2SON-4
U4, U6: SY80004DQD; DFN6-0.5-1.5X1.5X0.65MM; MPN SY80004DQD
U5: W25Q128JWSIQ; SOIC-8_5.23x5.23mm_P1.27mm
X1: 24MHz; 4P2016

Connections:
1V8: C13.1, C19.2, C20.1, C21.1, C28.1, C29.2, Q1.1 (G), Q2.1 (G), R5.1, R21.2, R22.2, R25.1, TP2.1 (T), U1.F3 (VDDIO_SIF1), U1.G3 (VDDA_RX), U1.H5 (VDDA_TX), U1.L2 (VDDIO_SIF2), U3.1 (OUT), U5.8 (VCC)
/0V9: C4.1, C7.1, L1.2, U1.L4 (DCDC_OUT)
BOOTOPT0: D3.1 (K), R11.1, U1.F4 (BOOT_OPT)
GND: C1.2, C2.2, C3.2, C4.2, C5.2, C6.2, C7.2, C8.1, C9.2, C10.2, C11.1, C13.2, C14.2, C15.1, C17.2, C18.2, C19.1, C20.2, C21.2, C22.2, C23.2, C24.1, C25.1, C26.2, C27.1, C28.2, C29.1, C30.1, C31.2, C34.2, C35.1, C37.1, C39.1, D5.1, D6.1, D7.1, D8.1, J1.A1_B1_A12_B12 (GND), J1.S1 (SHIELD), J2.1, J2.4, J2.7, J2.10, J2.MP (MountPin), J3.4, J3.MP (MountPin), J5.S1 (SHD1), J5.S2 (SHD2), J5.S3 (SHD3), J5.S4 (SHD4), J5.T6 (VSS), LED2.1 (K), M1.13 (GND), MIC1.4 (GND), MIC1.5 (L/R), MIC1.6 (GND), Q3.2 (S), R2.2, R3.2, R10.2, R11.2, R23.2, R26.1, R34.1, R37.2, RST1.2, TP3.1 (T), U1.C5 (GND1), U1.G4 (GND2), U1.H3 (GND3), U1.L3 (GND4), U1.M2 (GND5), U1.M4 (GND6), U2.2 (GND), U2.17 (EPAD), U3.2 (GND), U3.T (GND), U4.4 (GND), U5.4 (GND), U6.4 (GND), X1.2 (1), X1.4 (3)
GROVE_5V_IN: C18.1, C34.1, C35.2, J3.3, R14.1, R15.1, R31.2, R32.2, U6.6 (IN)
I2CS0_SCL/5V: J3.1, Q4.3 (D), R14.2
I2CS0_SDA/5V: J3.2, Q5.3 (D), R15.2
M_3V3_SCL: J2.13, Q1.3 (D), R19.2
M_3V3_SDA: J2.14, Q2.3 (D), R20.2
unnamed: BOOT1.2, R4.2
unnamed: D1.2 (A), R36.2
unnamed: C9.1, C10.1, C27.2, D2.1 (K), D4.1 (K), R6.2, R8.2, U4.6 (IN)
unnamed: BOOT1.1, D3.2 (A), R36.1
unnamed: J1.A5 (CC1), R2.1
unnamed: J1.B5 (CC2), R3.1
unnamed: LED1.2 (A), R38.1
unnamed: LED1.1 (K), Q3.3 (D)
unnamed: LED2.2 (A), R24.2
unnamed: M1.12 (3V3), R39.2
unnamed: MIC1.2 (CLK), R29.1
unnamed: MIC1.3 (DATA), R30.1
unnamed: Q3.1 (G), R37.1, R40.2
unnamed: R10.1, U1.E4 (TEST_MODE)
unnamed: L1.1, U1.L5 (VX1)
unnamed: C14.1, R35.1, U1.G2 (XTAL_24M_I), X1.3 (4)
unnamed: C15.2, R35.2, U1.F1 (XTAL_24M_O), X1.1 (2)
unnamed: C16.2, U2.13 (RTS)
unnamed: R8.1, U4.1 (EN)
unnamed: C32.1, R16.1, R26.2, U4.3 (FB)
unnamed: L2.1, U4.5 (LX)
unnamed: R6.1, U4.2 (PG)
unnamed: R31.1, U6.1 (EN)
unnamed: C36.1, R33.1, R34.2, U6.3 (FB)
unnamed: L3.1, U6.5 (LX)
unnamed: R32.1, U6.2 (PG)
PA0/3V3: M1.1 (D0/A0), U1.D4 (PA0)
PA1/VMUTE/3V3: J2.11, U1.C4 (PA1)
PA2/I2CS0_SCL/3V3: M1.6 (D5/SCL), Q4.2 (S), R1.1, R17.2, U1.A4 (PA2)
PA3/I2CS0_SDA/3V3: M1.5 (D4/SDA), Q5.2 (S), R13.1, R18.2, U1.B4 (PA3)
PB0/RX0/3V3: U1.A5 (PB0), U2.4 (TXD)
PB1/TX0/3V3: U1.B5 (PB1), U2.5 (RXD)
PB2/SSPIM_DO/3V3: D7.2, J5.T3 (CMD), M1.11 (D10/MOSI), R12.2, U1.N5 (PB2)
PB3/SSPIM_DI/3V3: D5.2, J5.T7 (DAT0), M1.10 (D9/MISO), R9.2, U1.M3 (PB3)
PB4/SSPIM_SCLK/3V3: D6.2, J5.T5 (CLOCK), M1.9 (D8/SCK), R27.2, U1.N4 (PB4)
PB5/SSPIM_~CS/3V3: D8.2, J5.T2 (CD/DAT3), R28.2, U1.N3 (PB5)
PB6/UART1_RX/3V3: M1.7 (D6/TX), U1.N1 (PB6)
PB7/UART1_TX/3V3: M1.8 (D7/RX/SS), U1.M1 (PB7)
PB8/3V3: M1.3 (D2/A2), U1.L1 (PB8)
PB9/PDM_CLK/3V3: R29.2, U1.F5 (PB9)
PB10/PDM_DATA0/3V3: R30.2, U1.G5 (PB10)
PB11/3V3: M1.2 (D1/A1), U1.J3 (PB11)
QSPI_CLK: U1.C2 (QSPI_CLK), U5.6 (CLK)
QSPI_CS: R5.2, U1.B2 (QSPI_CS), U5.1 (~CS)
QSPI_D0: U1.B1 (QSPI_DIO0), U5.5 (DI(IO0))
QSPI_D1: U1.D3 (QSPI_DIO1), U5.2 (DO(IO1))
QSPI_D2: U1.A1 (QSPI_DIO2), U5.3 (IO2)
QSPI_D3: U1.E3 (QSPI_DIO3), U5.7 (IO3)
RST: C3.1, C16.1, M1.4 (D3/A3), R7.1, RST1.1, U1.E5 (RESETN)
RX_CK_N: J2.8, U1.E2 (RX_CKN)
RX_CK_P: J2.9, U1.F2 (RX_CKP)
RX_D0_N: J2.2, U1.D2 (RX_DN0)
RX_D0_P: J2.3, U1.C1 (RX_DP0)
RX_D1_N: J2.5, U1.D1 (RX_DN1)
RX_D1_P: J2.6, U1.E1 (RX_DP1)
SEN_D1/SD~INSERT: J5.G1 (SWITCH), R25.2, U1.G1 (SEN_D1)
SEN_I2CM_SCL: Q1.2 (S), R21.1, U1.A3 (SEN_I2CM_SCL)
SEN_I2CM_SDA: Q2.2 (S), R22.1, U1.B3 (SEN_I2CM_SDA)
UD+: J1.A6 (D+), J1.B6 (D+), U2.7 (D+)
UD-: J1.A7 (D-), J1.B7 (D-), U2.8 (D-)
USER_LED/1V8: R40.1, U1.K2 (SEN_D2)
USR_BTN/1V8: D1.1 (K), R23.1, U1.H1 (SEN_D0)
V33IO: C2.1, C31.1, U2.1 (VIO), U2.6 (V3)
VBUS: C1.1, C30.2, D4.2 (A), J1.A4_B4_A9_B9 (VBUS), U2.3 (VDD5), U2.9 (VBUS)
VCC_3V3: C5.1, C6.1, C8.2, C11.2, C17.1, C22.1, C23.1, C24.2, C25.2, C26.1, C32.2, C36.2, C37.2, C39.2, J2.15, J5.T4 (VDD), L2.2, L3.2, MIC1.1 (VDD), Q4.1 (G), Q5.1 (G), R1.2, R4.1, R7.2, R9.1, R12.1, R13.2, R16.2, R17.1, R18.1, R19.1, R20.1, R24.1, R27.1, R28.1, R33.2, R38.2, R39.1, TP1.1 (T), U1.D5 (VDDIO_AON), U1.M5 (VDDA_DCDC), U1.N2 (VDDIO_PIF), U3.3 (EN), U3.4 (IN)
VMAIN: D2.2 (A), M1.14 (VUSB)

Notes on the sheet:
MIPI CSI
AON 3V3
MIPI DSI
PIF 3V3
SIF only 1V8
Imax=600mA
23/11/14
Grove - Vision AI Module V2
JN.FUONG

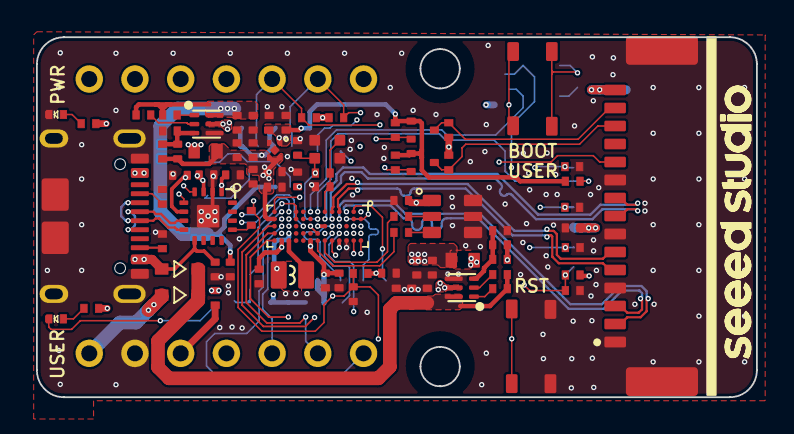
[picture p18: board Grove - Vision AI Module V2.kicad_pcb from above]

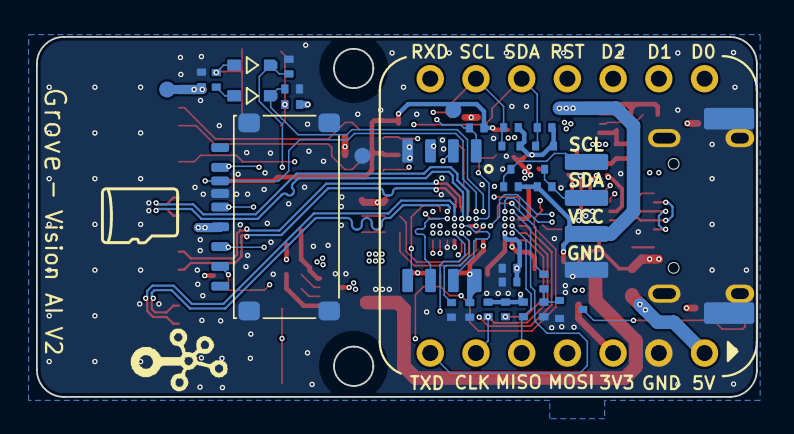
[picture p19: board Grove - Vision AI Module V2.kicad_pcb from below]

Board: 4 copper layers, 40.0 x 20.0 mm, 112 parts (31 on the bottom side), 75 nets.

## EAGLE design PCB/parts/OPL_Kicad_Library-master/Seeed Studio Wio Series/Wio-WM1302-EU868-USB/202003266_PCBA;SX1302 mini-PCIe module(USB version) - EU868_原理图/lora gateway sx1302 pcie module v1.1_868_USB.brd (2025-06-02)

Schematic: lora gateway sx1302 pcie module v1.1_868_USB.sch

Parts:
ANT1: U.FL-R-SMT-1(10); U-FL3P-SMD-2.6X2.6X1.0MM
ANT2: DNP; U-FL3P-SMD-2.6X2.6X1.0MM
C1, C12, C15, C19, C23, C25, C26, C29, C32, C41, C43, C45, C65, C67, C80, C83, C86, C88: 100nF; C0402
C2, C75: 2.2pF; C0402
C3, C92: 10uF; C0603
C4, C8, C11, C16, C17, C18, C64: 56pF; C0402
C5, C6, C9, C10: 3.6pF; C0402
C7, C91: 5.6pF; C0402
C13, C20, C21, C24, C28, C35, C39, C40, C42, C44, C47, C48, C76, C87, C89: 1uF; C0402
C14, C38, C57, C66, C81, C84: 10pF; C0402
C22, C27, C33: 10uF; C0603@1
C30, C56, C74, C77, C78, C79: DNP; C0402
C31: DNP; C0603@1
C34, C46, C63: 470nF; C0402
C36: 47nF; C0402
C37: 47pF; C0402
C49: 4.7uF; C0603
C50, C62, C85: 10nF; C0402
C51: 1nF; C0402
C52, C55: 100pF; C0402
C53, C60, C61: 3.3pF; C0402
C54: 39pF; C0402
C58: 1.3pF; C0402
C59, C68, C73: 1.8pF; C0402
C69, C70, C71, C72: 10uF; C0805
C82: 2.7pF; C0402
C90: 2.2uF; C0603
D1, D4: Green; LED-0402
D2: Red; LED-0402
D3: Blue; LED-0402
D5: LXES15AAA1-153; ESD-0402
D6: DNP; ESD-0402
D7: BAT54XV2T1G; SOD-523
FB1: BLM15PD121SN1D; F0402
J1: DNP; PCIE52P-0.8-50.95X30MM
L1: LQP15MN1N2B02D; L0402
L2: LQW15AN6N8G00D; L0402
L4: 0R; F0603
L5: LQH44PN1R0NP0L; L4.4X3.0MM
L6, L14, L20: MLZ2012M150WT; L0805
L7, L15, L18, L21: DNP; L0402
L8: LQW15AN3N0B00; L0402
L9: LQW15AN47NJ00D; L0402
L10: LQW15AN2N5B00D; L0402
L11: LQW15AN4N7C00D; L0402
L12, L13: LQW15AN12NG00D; L0402
L16: LQW15AN7N5G00D; L0402
L17, L24: LQW15AN5N6C10D; L0402
L22: LQW15AN15NG00D; L0402
Q8: CJ2101; SOT-323
Q10: CJ2102; SOT-323
R1, R4, R33, R34, R38, R42, R57, R65, R71: 10k; R0402
R2, R7: 0R; R0603
R3, R8, R11, R12, R43, R44, R46, R49, R51, R55, R56, R59, R60, R61, R62, R63, R67, R70, R72, R73, R74, R75, R76, R81: DNP; R0402
R5, R10, R14, R15, R16, R39, R40, R41: 100R; R0402
R6, R9, R37: 220R; R0402
R13, R35, R52: DNP; R0603
R17, R18, R19, R20, R21, R22, R23, R24, R25, R26, R27, R28, R29, R36, R45, R48, R50, R53, R54, R69, R77: 0R; R0402
R30, R31, R32: 680R; R0402
R47, R79: 1k; R0402
R58, R68: 4.7k; R0402
R64, R66: 22R; R0402
R78, R82: 100k; R0402
R80: 10R; R0402
R83, R87: 200k_1%; R0402
S1, S2, S3, S4, S5, S6: 323030226; SHIELD_CLIP
TP1, TP2, TP3, TP4, TP5, TP6, TP7, TP8, TP9, TP10, TP14: TEST-POINT-35; TP_3535
TP15: TEST-POINT'4545'; TP-D45MIL
U1: SX1302IMLTRT; QFN68-0.35-7X7X0.75MM
U2, U8, U10: HDF866A3-S6; FILTER6P-1.1-3X3X1.3MM
U3, U4: DNP; SOT-23-5
U5, U7: SX1250IMLTRT; QFN24G-0.5-4X4MM
U6: MP2161GJ; TSOT23-8
U9: SKY66420-11; MODULE16P-0.5-3X3X0.75MM
U11: SX1262IMLTRT; QFN24G-0.5-4X4MM
U12: STM32L412K8U6; UFQFPN32-0.5-5X5MM
U13: STTS751; UDFN-6L
X1: DSB221SDN; X4-SMD-2.5X2.0X1.0MM
X3: 32.768kHz; X2-SMD-3.2X1.5X0.55MM

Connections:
32MHZ: R6.2, R9.2, R37.2, X1.3 (OUT)
1302_CS: R33.2, R43.1, U1.1 (HOST_CSN), U12.10 (PA4)
1302_RESET: C1.2, D7.-, R1.2, U1.7 (RESET), U12.8 (PA2)
1302_RESET_HOST: D7.+, R59.1
CONFIG_OK: R31.1, U1.66 (GPIO0)
DM: J1.36, R66.1
DP: J1.38, R64.1
FEM_CS: R14.2, R34.1, U1.10 (RADIO_CTRL0), U3.3 (CE)
FEM_PA_ON: R15.2, U1.16 (RADIO_CTRL4)
GND: ANT1.GND1, ANT1.GND2, ANT2.GND1, ANT2.GND2, C2.1, C3.1, C5.1, C7.1, C9.1, C12.1, C13.1, C15.1, C16.1, C17.1, C18.1, C19.1, C20.1, C21.1, C22.1, C23.1, C24.1, C25.1, C26.1, C27.1, C28.1, C29.1, C30.1, C31.1, C32.1, C33.1, C34.1, C35.1, C36.1, C37.1, C39.1, C40.1, C41.1, C42.1, C43.1, C44.1, C45.1, C46.1, C47.1, C48.1, C49.1, C50.1, C51.1, C52.1, C55.1, C56.1, C57.1, C58.1, C60.2, C61.2, C62.1, C63.2, C65.2, C67.2, C69.1, C70.1, C71.1, C72.1, C73.2, C74.2, C76.1, C77.2, C78.2, C80.1, C81.2, C82.2, C83.1, C84.2, C85.1, C86.1, C87.1, C88.1, C89.1, C90.1, C92.1, D1.-, D2.-, D3.-, D4.-, D5.1, D6.1, J1.4 (GND), J1.9 (GND), J1.15 (GND), J1.18 (GND), J1.21 (GND), J1.26 (GND), J1.27 (GND), J1.29 (GND), J1.34 (GND), J1.35 (GND), J1.37 (GND), J1.40 (GND), J1.43 (GND), J1.50 (GND), J1.S1 (GND), J1.S2 (GND), Q10.2 (S), R1.1, R4.1, R11.1, R12.1, R17.2, R53.1, R53.2, R54.1, R54.2, R55.1, R55.2, R57.2, R73.1, R74.1, R74.2, R87.1, S1.S1, S1.S2, S1.S3, S1.S4, S1.S5, S2.S1, S2.S2, S2.S3, S2.S4, S2.S5, S3.S1, S3.S2, S3.S3, S3.S4, S3.S5, S4.S1, S4.S2, S4.S3, S4.S4, S4.S5, S5.S1, S5.S2, S5.S3, S5.S4, S5.S5, S6.S1, S6.S2, S6.S3, S6.S4, S6.S5, TP3.T, U1.6 (GND), U1.9 (GND), U1.15 (GND), U1.24 (GND), U1.25 (GND), U1.39 (GND), U1.46 (GND), U1.55 (GND), U1.62 (GND), U1.69 (GND), U2.1 (GND), U2.3 (GND), U2.4 (GND), U2.6 (GND), U3.2 (VSS), U4.2 (VSS), U5.7 (GND), U5.20 (GND), U5.PAD, U6.4 (PGND), U6.6 (AGND), U7.7 (GND), U7.20 (GND), U7.PAD, U8.1 (GND), U8.3 (GND), U8.4 (GND), U8.6 (GND), U9.10 (GND), U9.12 (GND), U9.17 (EPAD), U10.1 (GND), U10.3 (GND), U10.4 (GND), U10.6 (GND), U11.2 (GND), U11.5 (GND), U11.8 (GND), U11.20 (GND), U11.PAD, U12.16 (VSS), U12.32 (VSS), U12.PAD, U13.4 (ADDR/!THERM), U13.5 (GND), X1.2 (GND)
HOST_CS0: J1.51, R43.2
HOST_CS1: J1.25, R51.2
HOST_IO1: J1.33, R61.2
HOST_IO2: J1.31, R63.2
HOST_IO3: J1.23
HOST_IO4: J1.8, R67.2
HOST_IO5: J1.10, R60.2
HOST_IO6: J1.12
HOST_MISO: R39.1, R44.2
HOST_MOSI: J1.49, R46.2
HOST_RST: J1.22, R59.2, R77.2
HOST_SCK: J1.45, R49.2
I2C_SCL: R68.2, R76.1, R81.1, U12.29 (PB6), U13.1 (SCL)
I2C_SDA: R58.2, R70.1, R75.1, U12.30 (PB7), U13.6 (SDA)
MCU_RESET: C85.2, R71.2, R77.1, TP5.T, U12.4 (NRST)
MISO: R44.1, R45.1, U1.2 (HOST_MISO), U11.16 (MISO)
MISO_A: U1.42 (RADIO_A_MISO), U5.16 (MISO)
MISO_B: U1.33 (RADIO_B_MISO), U7.16 (MISO)
MOSI: R5.2, R40.2, R46.1, R48.1
MOSI_A: U1.67 (RADIO_A_MOSI), U5.17 (MOSI)
MOSI_B: U1.19 (RADIO_B_MOSI), U7.17 (MOSI)
unnamed: C11.2, U9.2 (RX)
unnamed: TP15.T, U6.1 (PG)
unnamed: C8.1, R11.2, R52.2, U8.5 (OUT)
unnamed: C2.2, L11.2, R52.1, U8.2 (IN)
unnamed: C11.1, R13.2, U2.2 (IN)
unnamed: C4.2, U9.1 (TX)
unnamed: C68.1, C74.1, C75.2
unnamed: C65.1, L18.2, R36.2, U11.1 (VDD_IN)
unnamed: C66.2, R37.1
unnamed: L5.1, U6.3 (SW)
unnamed: R83.1, R87.2, U6.7 (FB)
unnamed: R3.1, R4.2, X1.1 (ENABLE)
unnamed: C14.1, U5.3 (XTA)
unnamed: C62.2, L4.1, R3.2, X1.4 (VDD)
unnamed: R5.1, U1.3 (HOST_MOSI)
unnamed: D4.+, R47.2
unnamed: R10.1, U1.4 (HOST_SCK)
unnamed: R82.2, U6.8 (EN)
unnamed: R8.1, U4.3 (CE)
unnamed: C14.2, R6.1
unnamed: L6.2, U5.8 (DCC_SW)
unnamed: C34.2, L6.1, L7.2, U5.6 (VREG)
unnamed: C64.1, C82.1, L24.2
unnamed: R19.1, U1.34 (RADIO_B_CLK_I)
unnamed: C16.2, R14.1, U9.4 (CSD)
unnamed: C38.1, U7.3 (XTA)
unnamed: C36.2, C37.2, L9.2, U5.1 (VR_PA)
unnamed: C38.2, R9.1
unnamed: L14.2, U7.8 (DCC_SW)
unnamed: C46.2, L14.1, L15.2, U7.6 (VREG)
unnamed: C54.2, L11.1
unnamed: C7.2, C53.2, C54.1, L10.2
unnamed: C4.1, C8.2, R12.2
unnamed: C17.2, R15.1, U9.5 (CPS)
unnamed: C18.2, R16.1, U9.6 (CTX)
unnamed: R17.1, U1.20 (SP_VALID)
unnamed: R18.1, U1.32 (RADIO_B_IQ3)
unnamed: R20.1, U1.35 (RADIO_B_IQ0)
unnamed: R24.1, U1.41 (RADIO_A_IQ3)
unnamed: R21.1, U1.36 (RADIO_B_IQ1)
unnamed: R22.1, U1.37 (RADIO_B_IQ4)
unnamed: R23.1, U1.38 (RADIO_B_IQ2)
unnamed: R25.1, U1.43 (RADIO_A_CLK_I)
unnamed: R26.1, U1.44 (RADIO_A_IQ0)
unnamed: R27.1, U1.45 (RADIO_A_IQ1)
unnamed: R28.1, U1.48 (RADIO_A_IQ4)
unnamed: R29.1, U1.49 (RADIO_A_IQ2)
unnamed: D3.+, R32.2
unnamed: D2.+, R31.2
unnamed: D1.+, R30.2
unnamed: Q8.1 (G), Q10.3 (D), R78.2
unnamed: C1.1, R80.1
unnamed: L1.1, U9.16 (VCC1)
unnamed: L2.1, L8.1, U9.13 (PA_OUT)
unnamed: C56.2, C57.2, L8.2, L16.1
unnamed: C58.2, L16.2, U9.11 (TX_IN)
unnamed: C59.2, C60.1, L17.1, U9.9 (ANT)
unnamed: C61.1, C91.1, L17.2, L24.1
unnamed: C66.1, U11.3 (XTA)
unnamed: ANT1.D, C64.2, D5.2
unnamed: R35.2, R62.1, R69.2, U10.2 (IN)
unnamed: C63.1, L18.1, L20.1, U11.7 (VREG)
unnamed: R35.1, U9.7 (LNA_IN), U10.5 (OUT)
unnamed: L20.2, U11.9 (DCC_SW)
unnamed: J1.47, R39.2
unnamed: R40.1, U11.17 (MOSI)
unnamed: R41.1, U11.18 (SCK)
unnamed: C6.1, C10.1, C75.1, R13.1, U2.5 (OUT)
unnamed: R69.1, U9.8 (RX_FLT)
unnamed: C78.1, C79.1, L21.2
unnamed: ANT2.D, C79.2, D6.2
unnamed: C59.1, C91.2
unnamed: C77.1, L21.1, R62.2
unnamed: R65.2, U13.2 (!EVENT)
unnamed: C52.2, FB1.1, L1.2, U9.15 (VCC0)
unnamed: R64.2, U12.22 (PA12)
unnamed: R66.2, U12.21 (PA11)
unnamed: C92.2, Q10.1 (G), R79.2
unnamed: R56.2, R57.1, U12.31 (BOOT0)
unnamed: R72.2, R73.2, U12.6 (PA0-CLK_IN)
unnamed: C81.1, U12.2 (PC14-OSC32_IN), X3.2
unnamed: C84.1, U12.3 (PC15-OSC32_OUT), X3.1
unnamed: J1.14, R76.2
unnamed: J1.16, R70.2
unnamed: J1.30, R81.2
unnamed: J1.32, R75.2
PPS: J1.19, TP2.T, U1.8 (PPS), U12.27 (PB4)
RADIO_A_CLK_32M: R25.2, R72.1, U5.14 (BUSY)
RADIO_A_CLK_O: R28.2, U5.11 (DIO5)
RADIO_A_CSN: U1.68 (RADIO_A_CSN), U5.19 (NSS)
RADIO_A_IQ_0: R26.2, U5.13 (DIO1)
RADIO_A_IQ_1: R27.2, U5.12 (DIO2)
RADIO_A_IQ_2: R29.2, U5.5 (DIO3)
RADIO_A_IQ_3: R24.2, U5.21 (DIO4)
RADIO_A_RESET: U1.13 (RADIO_CTRL3), U5.15 (NRESET)
RADIO_A_RFIN: C6.2, L12.2, U5.23 (RFI_N)
RADIO_A_RFIP: C5.2, L12.1, U5.22 (RFI_P)
RADIO_B_CLK_32M: R19.2, U7.14 (BUSY)
RADIO_B_CLK_O: R22.2, U7.11 (DIO5)
RADIO_B_CSN: U1.18 (RADIO_B_CSN), U7.19 (NSS)
RADIO_B_IQ0: R20.2, U7.13 (DIO1)
RADIO_B_IQ_1: R21.2, U7.12 (DIO2)
RADIO_B_IQ_2: R23.2, U7.5 (DIO3)
RADIO_B_IQ_3: R18.2, U7.21 (DIO4)
RADIO_B_RESET: U1.28 (RADIO_CTRL9), U7.15 (NRESET)
RADIO_B_RFIN: C10.2, L13.2, U7.23 (RFI_N)
RADIO_B_RFIP: C9.2, L13.1, U7.22 (RFI_P)
RFO: C53.1, L9.1, L10.1, U5.24 (RFO)
RX_ON: R32.1, U1.59 (GPIO4)
SCK: R10.2, R41.2, R49.1, R50.1
SCK_A: U1.65 (RADIO_A_SCK), U5.18 (SCK)
SCK_B: U1.21 (RADIO_B_SCK), U7.18 (SCK)
STM32_MISO: R45.2, U12.12 (PA6)
STM32_MOSI: R48.2, U12.13 (PA7)
STM32_SCK: R50.2, U12.11 (PA5)
SWCLK: TP7.T, U12.24 (PA14)
SWDIO: TP8.T, U12.23 (PA13)
SX1261_BUSY: R67.1, U11.14 (BUSY), U12.9 (PA3)
SX1261_CS: R42.1, R51.1, U11.19 (NSS), U12.14 (PB0)
SX1261_IO1: R61.1, U1.54 (GPIO7), U11.13 (DIO1), U12.15 (PB1)
SX1261_IO2: R63.1, U11.12 (DIO2)
SX1261_IO3: TP9.T, U11.6 (DIO3)
SX1261_RFIN: C68.2, L22.2, U11.22 (RFI_N)
SX1261_RFIP: C73.1, L22.1, U11.21 (RFI_P)
SX1261_RST: R38.1, R60.1, U11.15 (NRESET), U12.18 (PA8)
SX1302_GPIO8: U1.53 (GPIO8), U12.26 (PB3)
TX_ON: R30.1, U1.63 (GPIO2)
TX_RX_SW: R16.2, U1.12 (RADIO_CTRL2)
VCCIO: C3.2, C19.2, C20.2, C25.2, C28.2, C41.2, C42.2, C45.2, C47.2, C76.2, C80.2, C83.2, C86.2, C87.2, C88.2, C89.2, C90.2, Q8.3 (D), R33.1, R34.2, R56.1, R58.1, R65.1, R68.1, R71.1, R80.2, TP1.T, U1.14 (VCC_IO), U1.30 (VCC_IO), U1.47 (VCC_IO), U1.61 (VCC_IO), U12.1 (VDD), U12.5 (VDDA), U12.17 (VDD), U13.3 (VDD)
VCC_1V2: C12.2, C13.2, C23.2, C24.2, C29.2, C40.2, C43.2, C44.2, C71.2, C72.2, L5.2, R79.1, R83.2, TP14.T, U1.5 (VCC_CORE), U1.23 (VCC_CORE), U1.40 (VCC_CORE), U1.56 (VCC_CORE), U6.5 (OUT)
VCC_FEM: C26.2, C27.2, C49.2, C50.2, C51.2, C55.2, FB1.2, L2.2, R2.2, TP6.T, U3.5 (VOUT)
VCC_RADIO: C21.2, C32.2, C33.2, C35.2, C39.2, C48.2, C67.1, L4.2, L7.1, L15.1, R7.2, R36.1, R38.2, R42.2, TP10.T, U4.5 (VOUT), U5.2 (VDD_IN), U5.9 (VBAT_RF), U5.10 (VBAT_DIO), U7.2 (VDD_IN), U7.9 (VBAT_RF), U7.10 (VBAT_DIO), U11.10 (VBAT), U11.11 (VBAT_IO)
VIN: C15.2, C22.2, C30.2, C31.2, C69.2, C70.2, J1.2 (3V3), J1.24 (3V3), J1.39 (3V3), J1.41 (3V3), J1.52 (3V3), Q8.2 (S), R2.1, R7.1, R8.2, R47.1, R78.1, R82.1, TP4.T, U3.1 (VIN), U4.1 (VIN), U6.2 (VIN)

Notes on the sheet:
V1.0
Initial Release
2020/01/02
Vincent
50ohm Impedence
3.3V
300mA
1.2V
500mA
100mA
USB
868
915
SPI
For Power-up delay
V1.1
Add power up delay circuit at VCCIO
Add power up reset circuit for SX1302
Change pins refer to Semtech V3 Schematic
2021/02/18

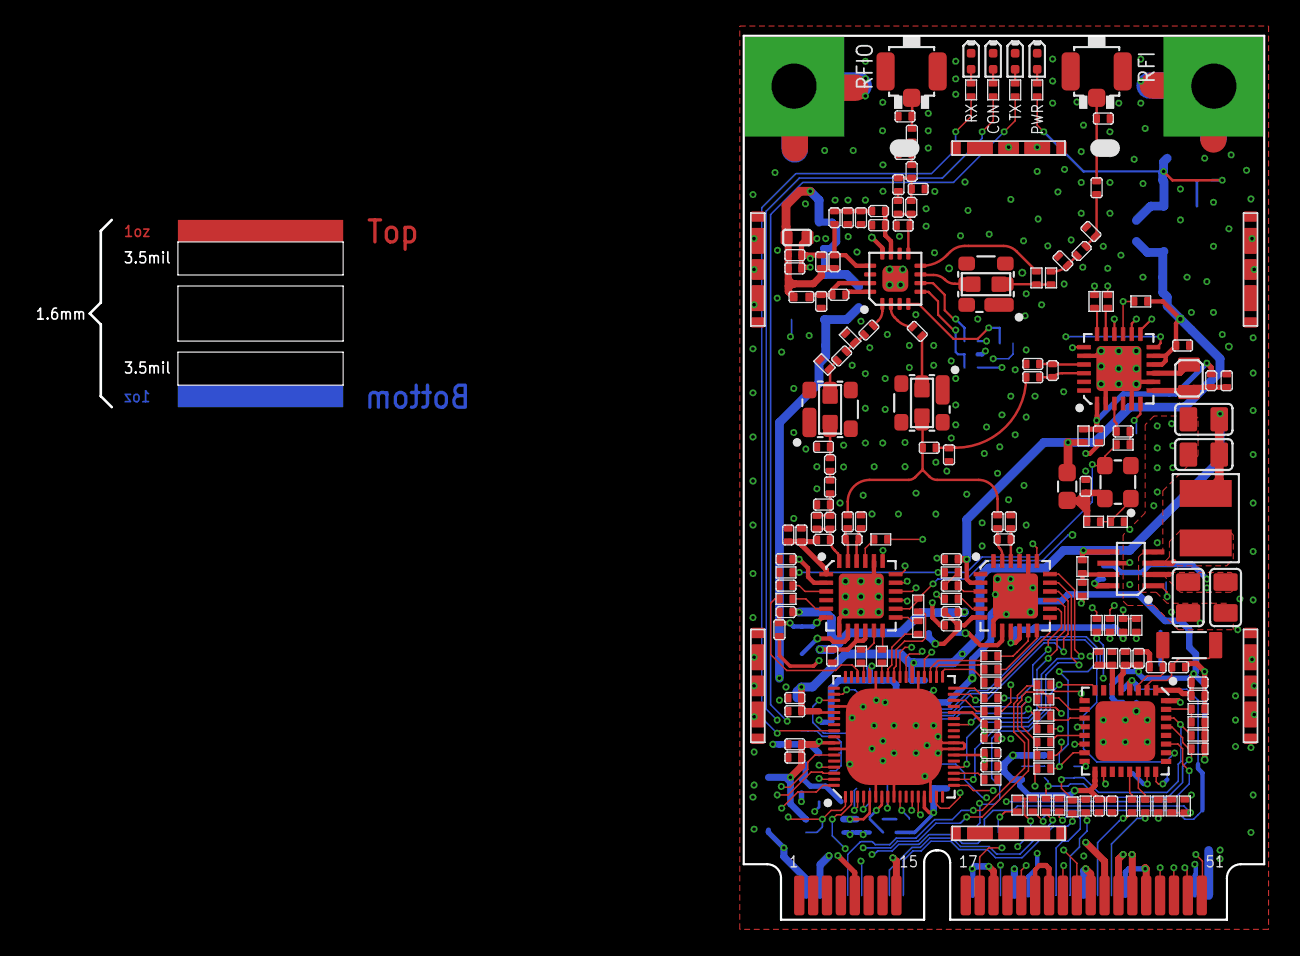
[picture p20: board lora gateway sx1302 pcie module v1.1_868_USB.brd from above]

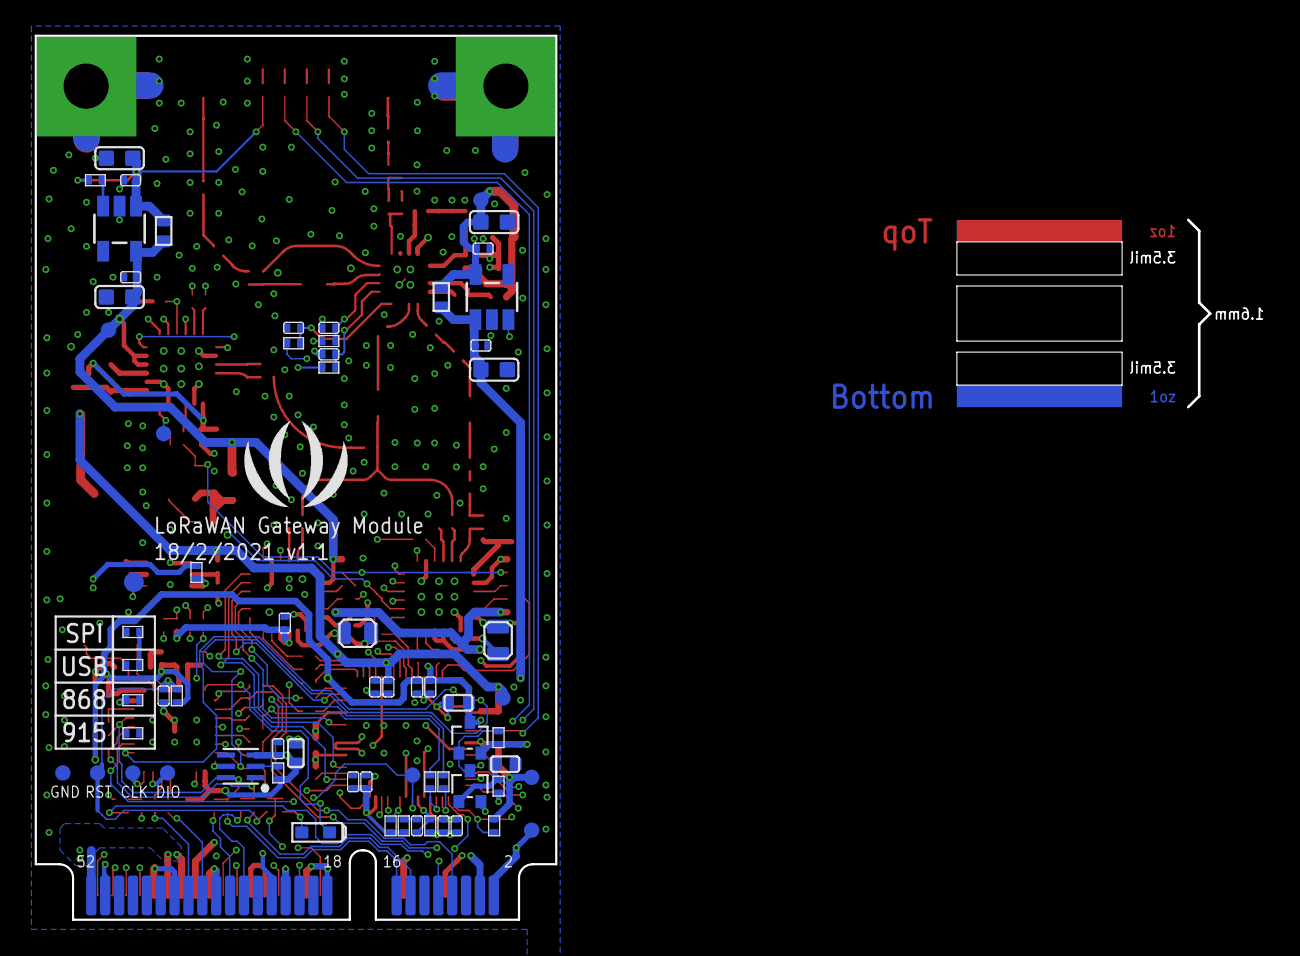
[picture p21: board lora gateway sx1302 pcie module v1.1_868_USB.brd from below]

Board: 4 copper layers, 30.0 x 51.0 mm, 244 parts (68 on the bottom side), 162 nets.

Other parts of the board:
U$45: SEEED-SILK-TNAME-280*268MIL

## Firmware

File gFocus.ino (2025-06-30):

#include <SPI.h>
#include <Arduino.h>

#define CMD_GET_DEVICE 0x01
#define CMD_SET_SETTINGS 0x2
#define CMD_GET_DATA 0x03

#define START_FLAG 0x7E
#define END_FLAG 0x7F
#define DEVICE_ID 0x01
#define RESPONSE_ERROR 0xFF
#define BUFFER_SIZE 64
#define QUEUE_SIZE 10 // Number of messages in FIFO

#define S_CLK 9
#define S_DIN 8
#define S_OUT A0

#define TIMER_INTERVAL_FQ 10  // 10 Hz

#define ACK 0xAA
#define NACK 0x55
#define MAX_RETRIES 3
#define ACK_TIMEOUT_MS 100

float exposureTime = 0.1f;  // 100 µs
uint16_t averagedData[128] = {0};
uint16_t tempBuffer[128];
uint8_t averageCount = 1;     // Average 1 run

// FIFO Queue for messages
typedef struct {
    uint8_t data[BUFFER_SIZE];
    int length;
} Message;

Message fifo_queue[QUEUE_SIZE];
int fifo_head = 0;
int fifo_tail = 0;

uint8_t Serial_buffer[BUFFER_SIZE];
int buffer_index = 0;

void checkAndExtractMessages();
void processSerialCommand();
uint8_t calculateCRC(uint8_t *args, int argCount);
void handleGetDevice();
void handleGetSettings(uint8_t average, float exposure);
void initializeLightSensor();
void onTimerInterrupt();
void runMeasurement(uint16_t* buffer);
void sendData(uint16_t* buffer, size_t length);
bool waitForAck(unsigned long timeout);
// FIFO Helper Functions
bool isFIFOFull() { return ((fifo_head + 1) % QUEUE_SIZE) == fifo_tail; }
bool isFIFOEmpty() { return fifo_head == fifo_tail; }

void ClockPulse() {
  delayMicroseconds(1);
  digitalWrite(S_CLK, HIGH);
  delayMicroseconds(1);
  digitalWrite(S_CLK, LOW);
}

void enqueueMessage(uint8_t *data, int length) {
    if (!isFIFOFull()) {
        memcpy(fifo_queue[fifo_head].data, data, length);
        fifo_queue[fifo_head].length = length;
        fifo_head = (fifo_head + 1) % QUEUE_SIZE;
    }
}

bool dequeueMessage(Message *msg) {
    if (!isFIFOEmpty()) {
        *msg = fifo_queue[fifo_tail];
        fifo_tail = (fifo_tail + 1) % QUEUE_SIZE;
        return true;
    }
    return false;
}

void setup() {
    digitalWrite(LED_BUILTIN, LOW);
    Serial.begin(115200);
    pinMode(S_CLK, OUTPUT);
    pinMode(S_DIN, OUTPUT);
    // analogReadResolution(12); // Set to 12 bits
    initializeLightSensor();
}

void loop() {
  // triggerCamera();
  // delay(1000);
    int ch = Serial.read();
    if (ch != -1) {
        Serial_buffer[buffer_index++] = (uint8_t)ch;

        if (buffer_index >= BUFFER_SIZE) {
            buffer_index = 0; // Prevent overflow
        }

        // Extract messages from buffer and store them in FIFO
        checkAndExtractMessages();
    }

    // Process the next available command in FIFO
    if (!isFIFOEmpty()) {
        processSerialCommand();
    }
}

void checkAndExtractMessages() {
    int startIdx = -1;
    int endIdx = -1;

    // Scan the buffer to find the first START_FLAG and END_FLAG
    for (int i = 0; i < buffer_index; i++) {
        if (Serial_buffer[i] == START_FLAG && startIdx == -1) {
            startIdx = i; // Mark the start of a valid message
        }
        if (Serial_buffer[i] == END_FLAG && startIdx != -1) {
            endIdx = i; // Found a complete message
            int messageLength = endIdx - startIdx + 1;

            // Store the valid message in FIFO
            enqueueMessage(&Serial_buffer[startIdx], messageLength);

            // Remove processed message from buffer
            memmove(Serial_buffer, &Serial_buffer[endIdx + 1], BUFFER_SIZE - (endIdx + 1));
            buffer_index -= (endIdx + 1);

            // Reset start/end markers and continue scanning
            startIdx = -1;
            endIdx = -1;
            i = -1; // Restart loop from beginning
        }
    }

    // If buffer is full but no complete message, reset to prevent overflow
    if (buffer_index >= BUFFER_SIZE) {
        buffer_index = 0;
        memset(Serial_buffer, 0, sizeof(Serial_buffer));
    }
}

void processSerialCommand() {
    Message msg;
    if (!dequeueMessage(&msg)) return;

    uint8_t command, length, receivedCRC, calculatedCRC;
    uint8_t channel_id;
    uint8_t average;
    float exposure;
    uint16_t value;

    if (msg.length < 4) return; // Ignore incomplete packets

    command = msg.data[1];
    length = msg.data[2];
    receivedCRC = msg.data[length];

    // Validate CRC
    calculatedCRC = calculateCRC(&msg.data[1], length - 1);
    if (calculatedCRC != receivedCRC) {
        Serial.write(RESPONSE_ERROR);
        return;
    }

    switch (command) {
        case CMD_GET_DEVICE:
            digitalWrite(LED_BUILTIN, HIGH);  // turn the LED on (HIGH is the voltage level)
            handleGetDevice();
            break;
        case CMD_SET_SETTINGS:
            if (length < 6) {
                Serial.write(RESPONSE_ERROR);
                return;
            }
            average = msg.data[3]; // uint8_t
            memcpy(&exposure, &msg.data[4], sizeof(float)); // Extract float from bytes
            exposureTime = exposure;
            averageCount = average;
            break;
        case CMD_GET_DATA:
            triggerCamera();
            break;
        default:
            Serial.write(RESPONSE_ERROR);
            break;
    }
}

uint8_t calculateCRC(uint8_t *args, int argCount) {
    uint8_t crc = 0;
    for (int i = 0; i < argCount; i++) {
        crc ^= args[i];
    }
    return crc;
}

void handleGetDevice() {
    uint8_t response[] = {CMD_GET_DEVICE, 0x01, DEVICE_ID};
    uint8_t crc = calculateCRC(response, 3);

    Serial.write(START_FLAG);
    for (int i = 0; i < 3; i++) {
        Serial.write(response[i]);
    }
    Serial.write(crc);
    Serial.write(END_FLAG);
}

void triggerCamera() {
  // Clear sum buffer if it's the first average cycle
  memset(averagedData, 0, sizeof(averagedData));

  for (int n = 0; n < averageCount; n++) {
    runMeasurement(tempBuffer);

    // Sum up results
    for (int i = 0; i < 128; i++) {
      averagedData[i] += tempBuffer[i];
    }
  }

  // Final average
  for (int i = 0; i < 128; i++) {
    averagedData[i] /= averageCount;
  }

  // Send data in four chunks of 32 values each
  for (int chunk = 0; chunk < 4; chunk++) {
    int start = chunk * 32;
    int retries = 0;
    bool success = false;

    while (retries < MAX_RETRIES) {
      sendData(&averagedData[start], 32);
      if (waitForAck(ACK_TIMEOUT_MS)) {
        success = true;
        break;
      } else {
        retries++;
      }
    }
  }
}

void runMeasurement(uint16_t* buffer) {
  digitalWrite(S_DIN, HIGH);
  ClockPulse();
  digitalWrite(S_DIN, LOW);

  unsigned int microSeconds = (unsigned int) exposureTime * 1000;
  delayMicroseconds(microSeconds);

  buffer[0] = analogRead(S_OUT);

  for (int i = 1; i < 128; i++) {
    ClockPulse();
    buffer[i] = analogRead(S_OUT);
  }
  ClockPulse();
  delayMicroseconds(20);
}

void sendData(uint16_t* buffer, size_t length) {
  // Total size: CMD (1) + LEN (1) + DATA (length) + CRC (1) + flags (2)
  size_t payloadSize = 1 + 1 + 1*length; 
  uint8_t response[payloadSize+3];

  // First packet: low bytes
  response[0] = CMD_GET_DATA;
  response[1] = length;

  for (size_t i = 0; i < length; i++) {
    response[2 + i] = buffer[i] & 0xFF;  // Low byte
  }


  uint8_t crc1 = calculateCRC(response, payloadSize);

  Serial.write(START_FLAG);
  Serial.write(response, payloadSize);
  Serial.write(crc1);
  Serial.write(END_FLAG);

  delayMicroseconds(1000);

  // Second packet: high bytes
  response[0] = CMD_GET_DATA;  // different command for clarity
  response[1] = length;
  
  for (size_t i = 0; i < length; i++) {
    response[2 + i] = (buffer[i] >> 8) & 0xFF;  // High byte
  }

  uint8_t crc2 = calculateCRC(response, payloadSize);

  Serial.write(START_FLAG);
  Serial.write(response, payloadSize);
  Serial.write(crc2);
  Serial.write(END_FLAG);
}

void initializeLightSensor() {
  // Clock out any excisting SI pulse through the CCD register
  for (int i = 0; i < 130; i++) {
    ClockPulse();
  }

  // Send an SI pulse and clock out the sensor register
  digitalWrite(S_DIN, HIGH);
  ClockPulse();
  digitalWrite(S_DIN, LOW);

  for (int i = 1; i < 128; i++) {
    ClockPulse();
  }
}

bool waitForAck(unsigned long timeout) {
  unsigned long startTime = millis();
  while (millis() - startTime < timeout) {
    if (Serial.available()) {
      int resp = Serial.read();
      if (resp == ACK) return true;
      if (resp == NACK) return false;
    }
  }
  return false;  // Timeout
}

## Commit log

2025-06-02 added drivers
    [DF11-12DS-2DSA--3DModel-STEP-1.STEP, Grove - Vision AI Module V2.kicad_pcb, Grove - Vision AI Module V2.kicad_sch, Grove_Vision_AI_V2_BOM.xlsx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]
2025-06-03 camera polling 5 times
2025-06-03 get name of focus stage
2025-06-03 CameraPollingTask added function snapOnce for calibration
2025-06-03 returning to home after calibration
2025-06-03 calibration step size 0.25um
2025-06-05 handshake protocol for sending camera data and cut up into 32 bytes
2025-06-17 XIAO board is added and fixed graph bugs
2025-06-24 private CMMCore for light sensor polling
2025-06-24 generic device in init module
2025-06-24 average to 1 and back to as camera devicee
2025-06-24 fix set property camera
2025-06-24 camera polling task
2025-06-24 attach and detatch
2025-07-01 added bom
    [bom.csv]
2025-12-05 updated readme and files
    [bom.csv, bom_external_components.csv, fgFocus-B_Cu.gbr, fgFocus-B_Mask.gbr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]
2025-12-05 readme assembly
2025-12-08 updated bom of enclosure
    [bom.csv]
2025-12-08 updated readme and bom with cost estimation
    [bom.csv, bom_external_components.csv]

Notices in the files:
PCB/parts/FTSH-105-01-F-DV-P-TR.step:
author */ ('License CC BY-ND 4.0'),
